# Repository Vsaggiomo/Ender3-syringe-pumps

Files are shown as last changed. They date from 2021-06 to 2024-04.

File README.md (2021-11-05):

# Ender 3 syringe pumps: 
open-source set of syringe pumps from an Ender 3 kit

**If you use the pump in your research, please cite:**

**Sander Baas, Vittorio Saggiomo,
Ender3 3D printer kit transformed into open, programmable syringe pump set,
HardwareX, Volume 10, 2021,
e00219, https://doi.org/10.1016/j.ohx.2021.e00219.**

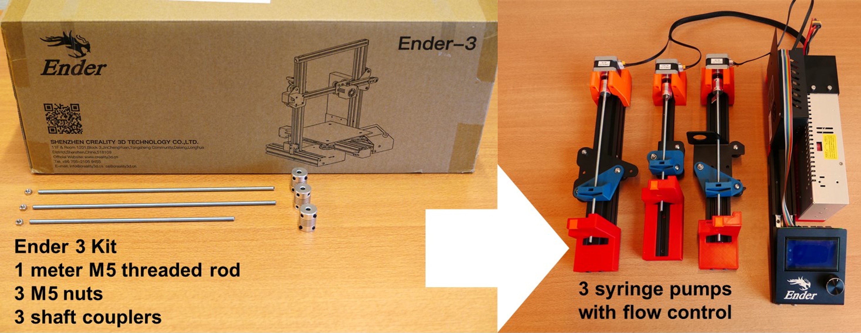
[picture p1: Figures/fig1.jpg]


Visit [**ChemRxiv**][2] for the preprint, and [**HardwareX**][3] for the published paper. 

A video of the project is here: https://www.youtube.com/watch?v=etUp4s1Bq-I

Ender 3 syringe pumps is an open source and open hardware device for converting an Ender 3 kit to a set of 3 syringe pumps. Almost everything needed for the build is the Ender 3 kit, even all the screws and the tools needed for the assembly. 
The only parts which needed to be bought are three 5x5 shaft couplers and M5 lead screw. 
All the 3D designs are in the /hardware folder. 

## Structure 
+ /hardware is a folder with the 3D printable files and a guide for the assembly 
+ /software is a folder with the instruction on how to use the pumps via gcode 
+ /videos are few video of the pumps in action

[1]: https://github.com/Vsaggiomo/Ender3-syringe-pumps/blob/main/Figures/fig1.jpg
[2]: https://chemrxiv.org/articles/preprint/Ender3_3D_Printer_Kit_Transformed_into_Open_Programmable_Syringe_Pump_Set/14718183 
[3]: https://doi.org/10.1016/j.ohx.2021.e00219

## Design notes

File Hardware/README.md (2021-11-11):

# Ender 3 syringe pumps: hardware

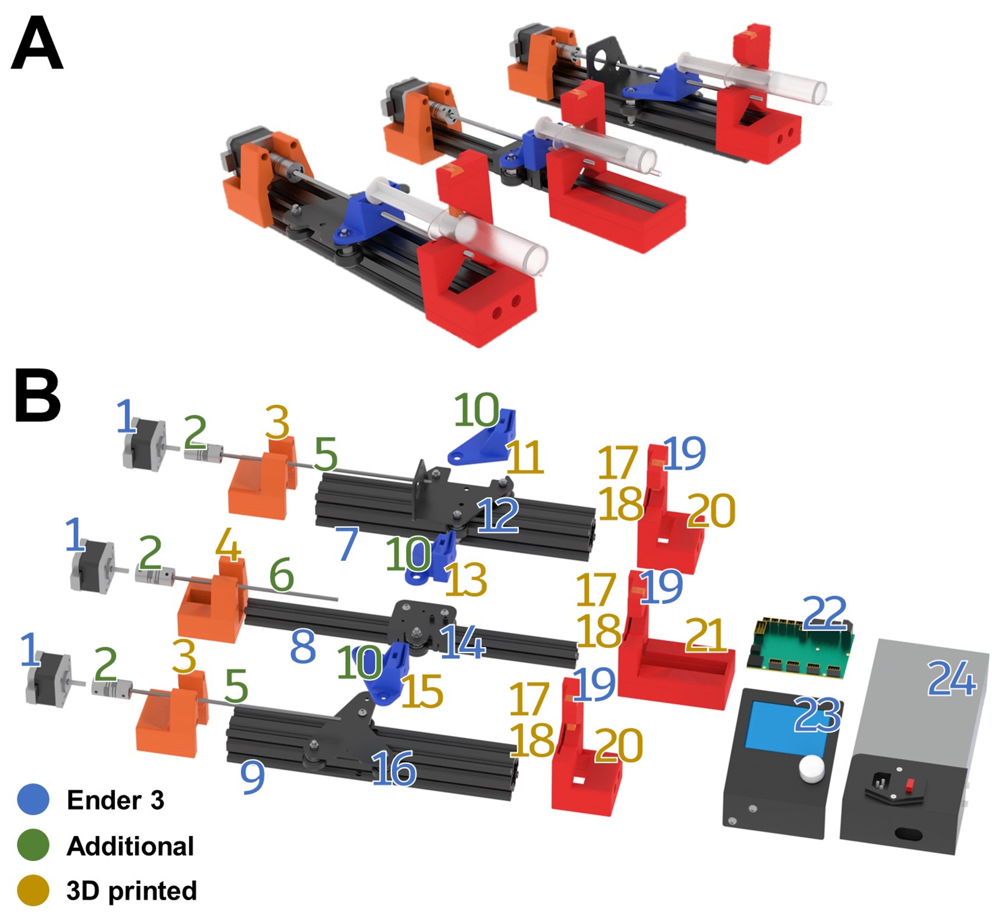
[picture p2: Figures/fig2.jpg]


+ STL and F3D contain the 3D printable files 
+ Ender 3 Syringe Pump Build Guide is the step by step guide to assemble the syringe pumps 

This design has been tested with Ender 3 and Ender 3 pro. It works also with the Ender 3 V2 with a small modification of the PSU mount, which can be found in the Ender3V2 directory. The Ender 3 V2 PSU mount was designed by Afonso Mendes (ammendes@igc.gulbenkian.pt) 

/STL/PressFitPulley.stl was designed by Jake_of_All_Trades https://www.thingiverse.com/thing:3593964/files 

UPDATE 05-11-2021: 50mL syringe adaptors are in /STL 

[1]: https://github.com/Vsaggiomo/Ender3-syringe-pumps/blob/main/Figures/fig2.jpg

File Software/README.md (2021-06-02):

# Ender 3 syringe pumps software 

+ Steps mL Calculation is an excel file for calculating the steps per mL of different syringes, using the diameter as input 
+ VideoS1 is a gcode example

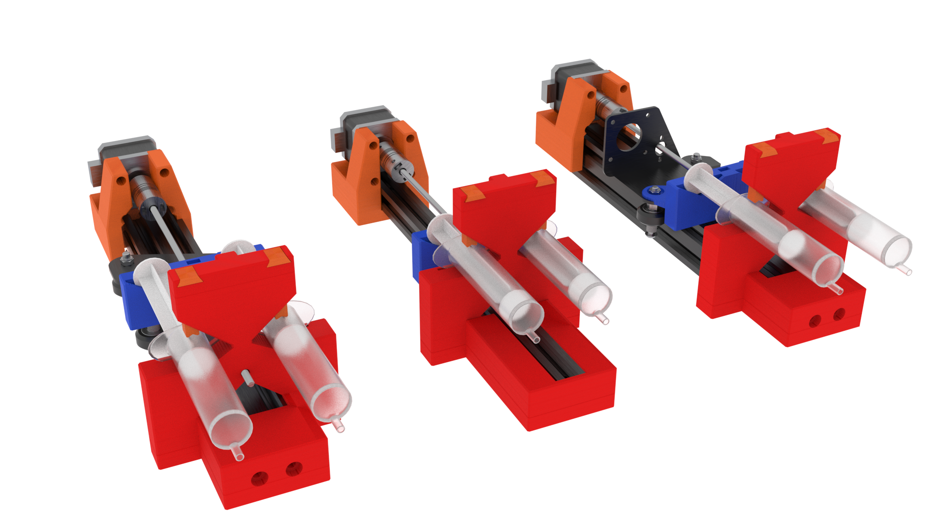
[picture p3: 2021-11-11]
Figures/double syringe.png

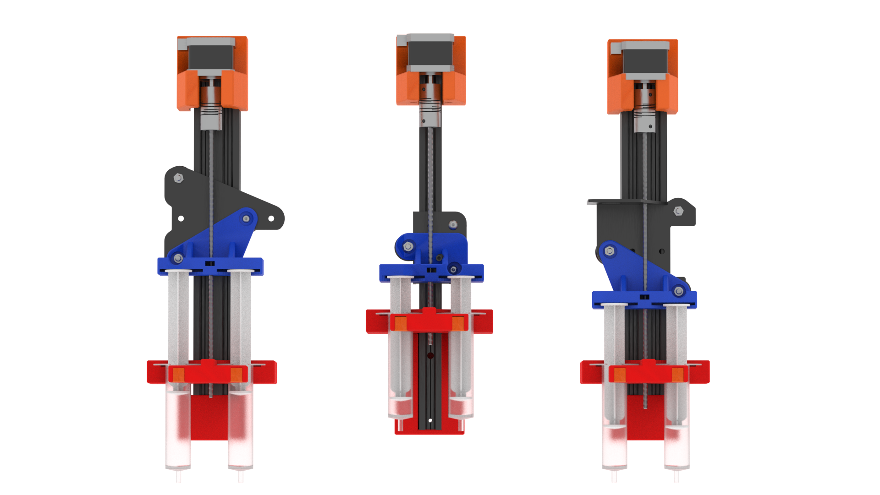
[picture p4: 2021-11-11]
Figures/double syinge2.png

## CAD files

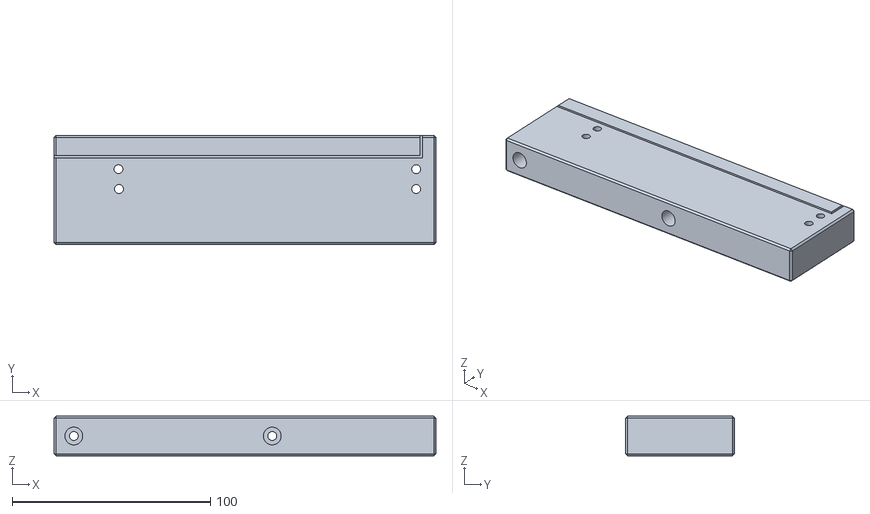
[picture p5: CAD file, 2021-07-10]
Hardware/Ender 3 V2/psu_mount_Ender3v2.stl
192.5 x 55.0 x 20.0

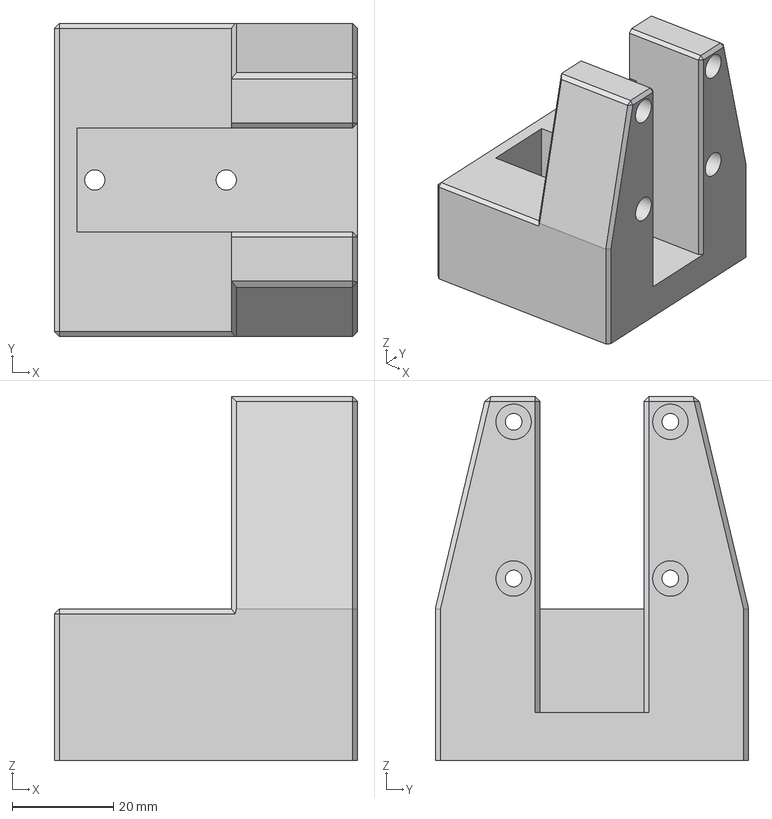
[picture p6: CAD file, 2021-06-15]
Hardware/STEP/E Stepper Mount v1.step
60.0 x 62.0 x 72.0 mm

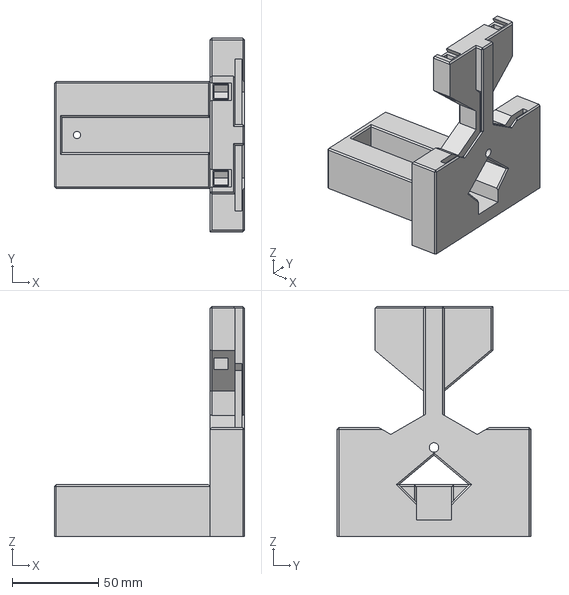
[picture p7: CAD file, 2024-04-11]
Hardware/STL/50 mL adaptors /E End Mount Dual 50 mL v1.step
110.0 x 112.0 x 133.0 mm

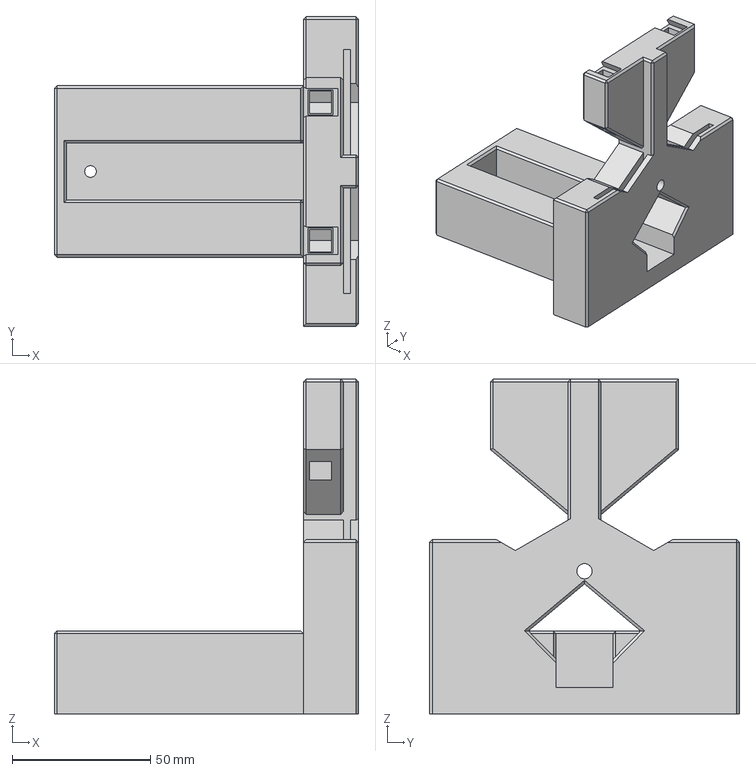
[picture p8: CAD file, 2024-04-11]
Hardware/STL/Double Syringe/E End Mount Dual v7.step
110.0 x 112.0 x 121.0 mm

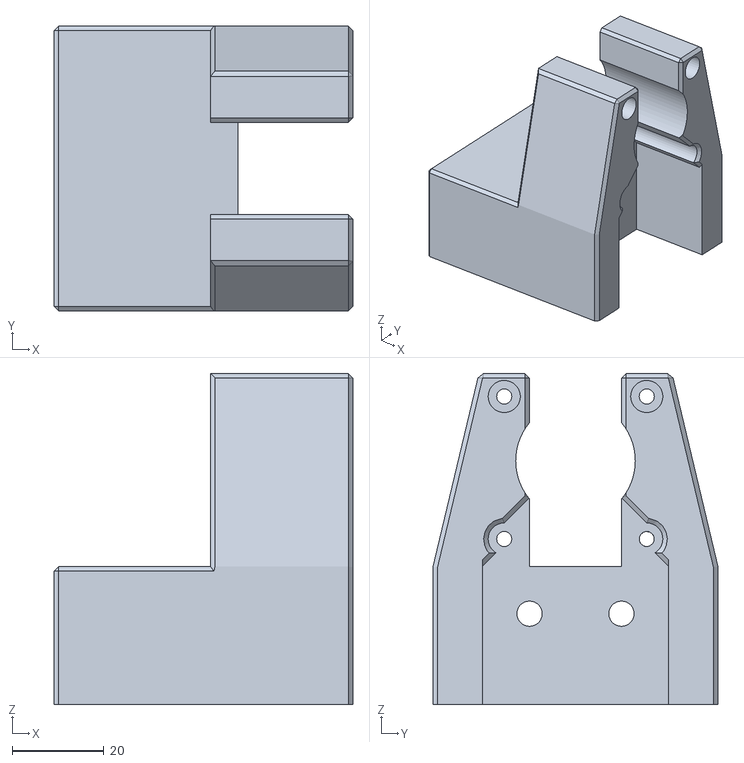
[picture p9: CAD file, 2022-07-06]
Hardware/STL/Large shaft coupler/X X Motor Stepper Mount Large Shaft Coupler v1.stl
65.0 x 62.0 x 72.0

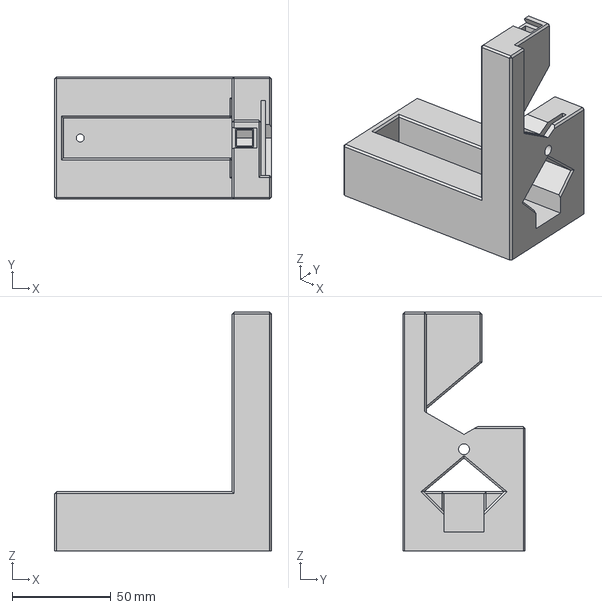
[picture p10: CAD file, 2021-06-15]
Hardware/STEP/E End Mount v1.step
110.0 x 62.0 x 121.0 mm

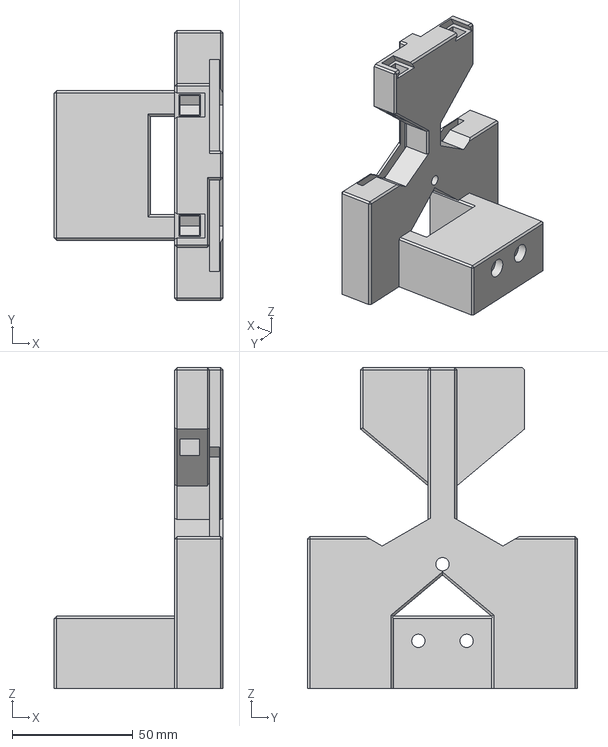
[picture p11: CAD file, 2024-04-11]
Hardware/STL/50 mL adaptors /X X Motor End Mount Dual 50 mL v4.step
70.0 x 112.0 x 133.0 mm

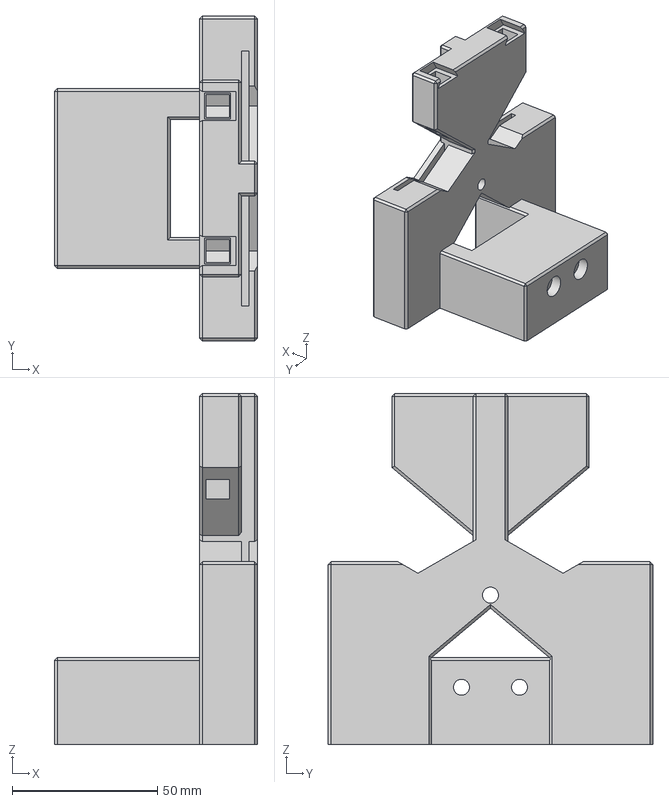
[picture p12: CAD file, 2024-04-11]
Hardware/STL/Double Syringe/X X Motor End Mount Dual v6.step
70.0 x 112.0 x 121.0 mm

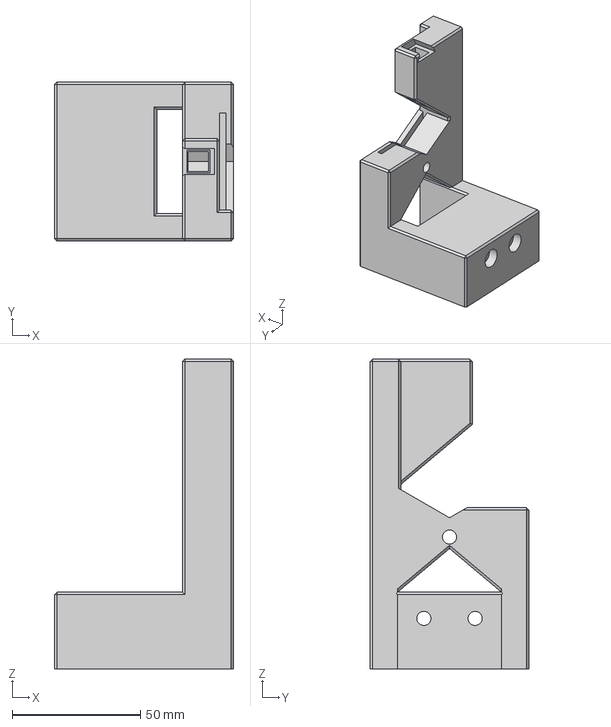
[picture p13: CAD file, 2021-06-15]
Hardware/STEP/X X Motor End Mount v1.step
70.0 x 62.0 x 121.0 mm

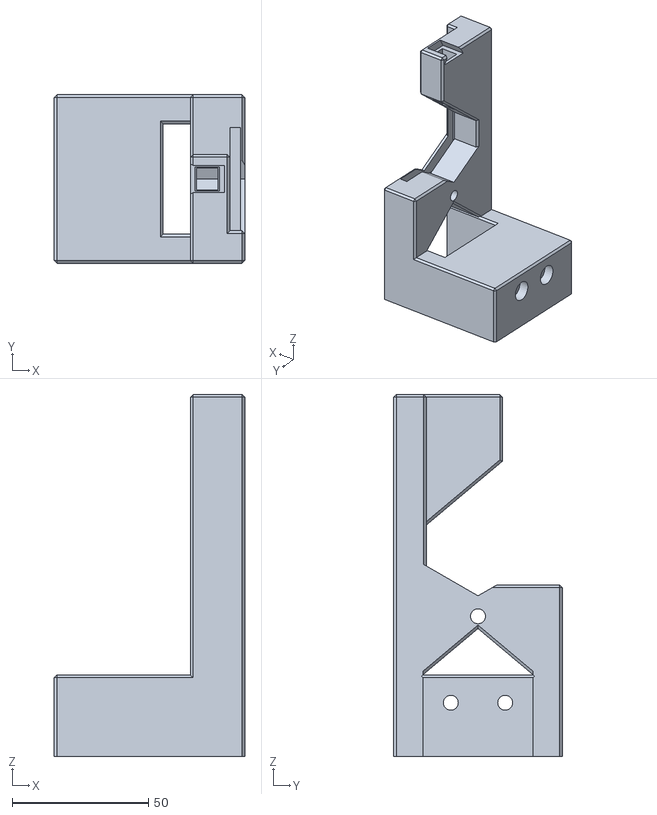
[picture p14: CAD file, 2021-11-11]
Hardware/STL/50 mL adaptors /X X Motor End Mount 50 mL.stl
70.0 x 62.0 x 133.0

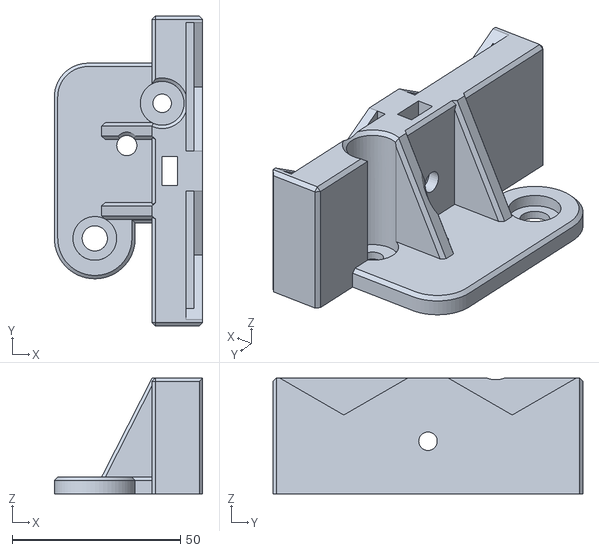
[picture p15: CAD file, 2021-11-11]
Hardware/STL/Double Syringe/E Slide Mount Dual.stl
44.0 x 92.0 x 34.4

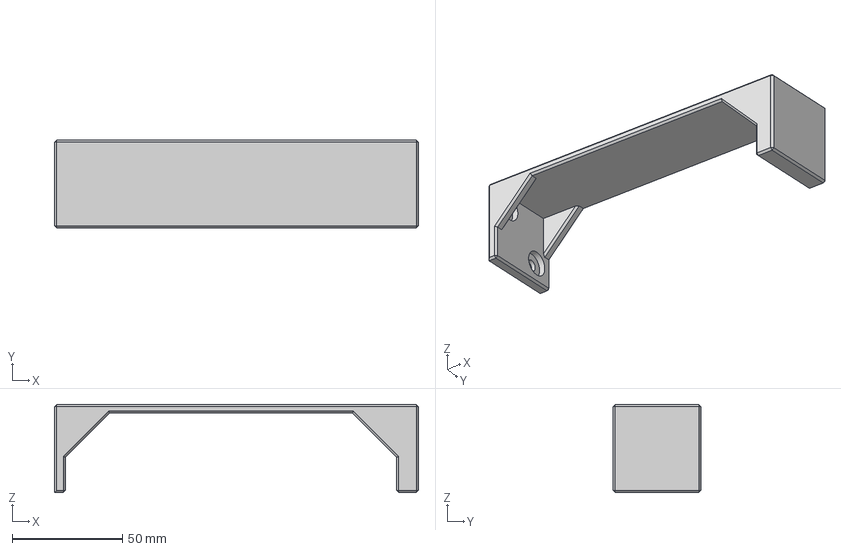
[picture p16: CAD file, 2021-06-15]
Hardware/STEP/Electronics Base v1.step
165.2 x 40.0 x 40.0 mm

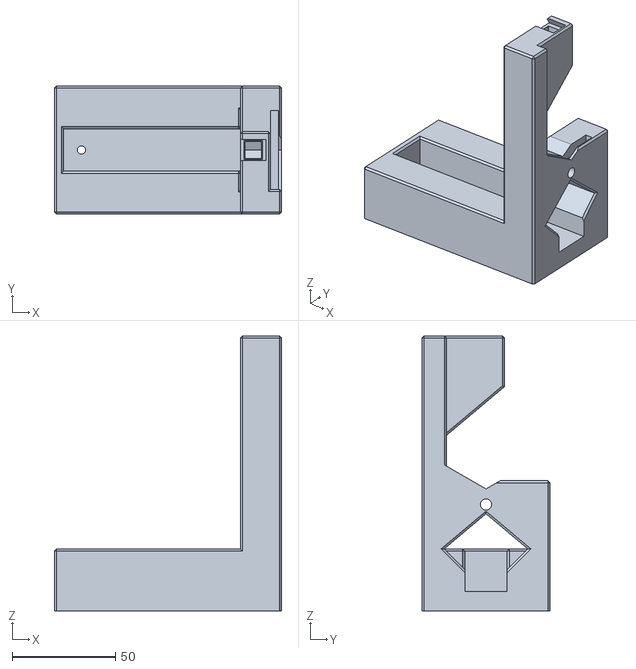
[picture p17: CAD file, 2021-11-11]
Hardware/STL/50 mL adaptors /E End Mount 50 mL.stl
110.0 x 62.0 x 133.0

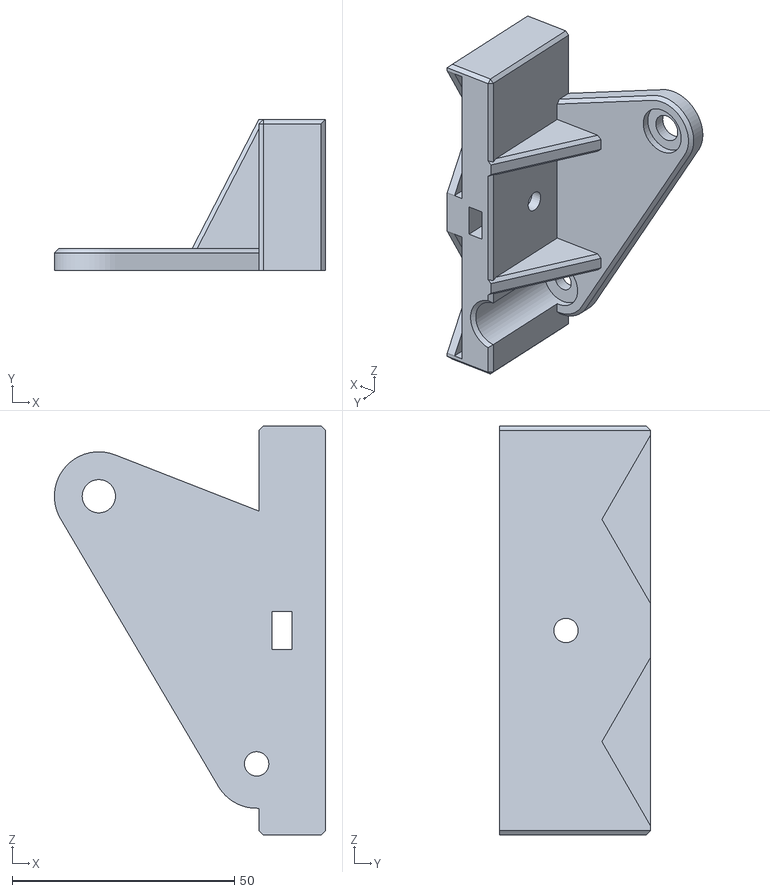
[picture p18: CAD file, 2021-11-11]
Hardware/STL/Double Syringe/X Motor Slide Mount Dual.stl
61.0 x 34.0 x 92.0

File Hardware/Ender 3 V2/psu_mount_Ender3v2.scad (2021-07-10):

$fa=5;
$fs=0.5;

difference(){
// Change this path to where you saved your original STL
import("/Users/ammendes/Documents/3D prints/Ender3_pumps/stl/PSU Mount v1.stl");

// Right screw hole
translate([182.5,28,0])
    cylinder(h=20, d=4.5);

// Left screw hole
translate([32.75,28,0])
    cylinder(h=20, d=4.5);

//Left screw head hole
translate([32.75,28,0])
    cylinder(h=7.5, d=9);

// Right screw head hole
translate([182.5,28,0])
    cylinder(h=7.5, d=9);

// Long horizontal gap
translate([0,43.5,15])  
    cube([184.5,1.3,5]);

// Short vertical gap
translate([184.5,43.5,15])
    cube([1.3,12,5]);
}

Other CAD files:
Hardware/STL/Large shaft coupler/E Stepper Mount Large Shaft Coupler v1.stl.stl
Hardware/STEP/X Motor Slide Mount v1.step
Hardware/STL/50 mL adaptors /X X Motor End Mount 50mL v2.stl
Hardware/F3D/50 mL adaptors/E End Mount 50 mL.f3d
Hardware/F3D/50 mL adaptors/E End Mount Dual 50 mL.f3d
Hardware/F3D/50 mL adaptors/X X Motor End Mount 50 mL.f3d
Hardware/F3D/50 mL adaptors/X X Motor End Mount Dual 50 mL.f3d
Hardware/F3D/Clamp Bar Long v1.f3d
Hardware/F3D/Clamp Bar Short v1.f3d
Hardware/F3D/Clamp Bar v1.f3d
Hardware/F3D/Double Syringe /E End Mount Dual.f3d
Hardware/F3D/Double Syringe /E Slide Mount Dual.f3d
Hardware/F3D/Double Syringe /X Motor Slide Mount Dual.f3d
Hardware/F3D/Double Syringe /X Slide Mount Dual.f3d
Hardware/F3D/Double Syringe /X X Motor End Mount Dual.f3d
Hardware/F3D/Dovetail Cap v1.f3d
Hardware/F3D/E End Mount v1.f3d
Hardware/F3D/E Slide Mount v1.f3d
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

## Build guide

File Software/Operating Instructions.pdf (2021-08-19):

Operating Instructions

The syringe pumps are controlled by the 3D printer motherboard, which is already flashed with Marlin software and therefore works with G-code. There are two ways of controlling the pumps: a) using a computer connected to the board via USB and using direct control software such as PronterFace or Octoprint, with the latter able to be used remotely via network. B) writing the G-code file, uploading it on a microSD card and using the printer interface for printing the file without the need of a computer attached to the pumps.
A G-code file is a set of instruction which Marlin interprets line by line and passes the operations to the motors. The file is a simple text file saved as .gcode. For controlling the pumps, a few G-code commands are needed:

M92 X<Steps per mm> Y<Steps per mm> Z<Steps per mm>

M92 should be at the start of the G-code, as this command will set the number of steps required for moving one axis one millimeter, which in the case of the Ender 3 motors/drivers and the M5x0.8 mm threaded rod is 4000 steps per mm. The Ender 3 uses stepper motors with a step angle of 1.8 °, or 200 steps per revolution. The TSMC2208 stepper drivers are set to 1/16 microsteps, which is the default setting for the Ender 3. The pitch of the leadscrew is 0.8 mm. This gives the value of 4000 steps per mm. However, as we are dealing with flows, we found that it is more user-friendly to change this command from steps per mm to steps per mL. This can be easily done by calculating the distance required to push a volume of 1 mL depending on the diameter of the syringe used. To do this, the inner diameter (I.D.) of the syringe needs to be determined. Next, the area of the plunger can be calculated. The linear syringe travel to deposit 1 mL can be calculated by dividing 1 cm³ by the plunger area (cm²
). Divide this number
by the steps per mm value (4000) to get the steps per mL. We have attached a simple calculator in the supplementary material to calculate the steps per mL using the diameter of a syringe as input. As an example, a 10 mL syringe has a diameter of 15.6 mm and the calculated steps required to move 1 mL are 20927, a 5 mL syringe has a diameter of 12.3 mm and the calculated
steps | are | 33663.
Another thing to take note of, is that in the normal configuration, the X and Y motors are inverted, so this should also be set in the M92 command by giving negative step/mm values. A M92 set up using two 5 mL syringes on the X and Z axes and a 10 mL syringe on the Y is therefore:

M92 X-33663 Y-20927 Z33663
This will set the number of steps per mL in such a way that the rest of the G-code will use this to calculate the pump movements.

M302 S0
This command will set the printer to move the motors without checking the temperature of the hot end. This is usually a 3D printer safety check for avoiding extruding material when there are some problems with the hot end. In this case the hot end is detached, so there is no risk of thermal runaway.

M211 S0
This command will disable the endstops which may cause problems as they are not connected.

G91
Use relative positioning. This is important when multiple movements are used, otherwise the motors will start from a 0.0.0 position and use that as reference point.

G4 S<time in seconds>
Pause the commands for a set amount of time.

G1 X<mL> Y<mL> Z<mL> F<mL/min>
This is the command to move the syringe pumps at certain flowrates. As we set up the steps/mL in the M92 command, now all the G1 codes are in mL/min. This can be a positive number or a negative number, positive for pushing and negative for retracting.

For example:
G1 X0.5 F1
Will use syringe pump X and will deliver 0.5 mL of liquid at a speed of 1 mL per minute. Multiple syringes can be used at the same time:
G1 X0.5 Y0.5 Z0.5 F1
Will deliver, at the same time, 0.5 mL of liquid from the pumps on X, Y, and Z at a speed of 1 mL/min
For using different flow speed for different pumps, the total amount of liquid should be calculated taking in account that all the pumps will reach the end at the same time. For example: G1 X2 Y1 Z2 F1
Will deliver the set amount of liquid at different flow speed, using 1ml/min on Y, and 2mL/min on X and Z.
For commenting on G-code files the “;” character should be used. This can be useful in commenting the G-code with metadata.

An example of full G-code (VideoS1):
; Experiment 01 20/05/2021
; 10 mL syringes on the three pumps
M92 X-20927 Y-20927 Z20927 ; set the proper steps/mL for the 10mL syringe M302 S0 ; print without checking temperature
G91 ; relative positioning
; deliver 1mL at 2mL/min sequentially
G1 X1 F2
G1 Y1 F2
G1 Z1 F2
; wait for 10 seconds
G4 S10
; deliver 1mL on X and Z at 1mL/min, 2mL on Y at 2mL/min G1 X1 Y2 Z1 F1
; wait 10 seconds
G4 S10
; deliver 1mL at 2mL/min sequentially G1 Z1 F2
G1 Y1 F2
G1 X1 F2

Without previous knowledge in programming and in a few lines of G-code it is possible to program the syringe pumps to do multiple operations. This file can now be saved as .gcode, uploaded on a microSD card, and run on the Ender 3 syringe pumps. Or it can be sent using a computer connected to the USB.
G-code files can be easily shared between labs for improving reproducibility of experiments.

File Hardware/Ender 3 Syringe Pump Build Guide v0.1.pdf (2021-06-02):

## Ender 3 Syringe Pump Build Guide

In this build guide, the build process of the Ender 3 based pump system will be explained. Assembly instructions, as well as indications of how to disassemble and reuse existing parts will be given. The guide consists of 37 steps and will result in three pump channels, as well as a Control Unit.

### Step 1: Layout

Start with laying out all the parts and part bags included in the kit (figure 1).

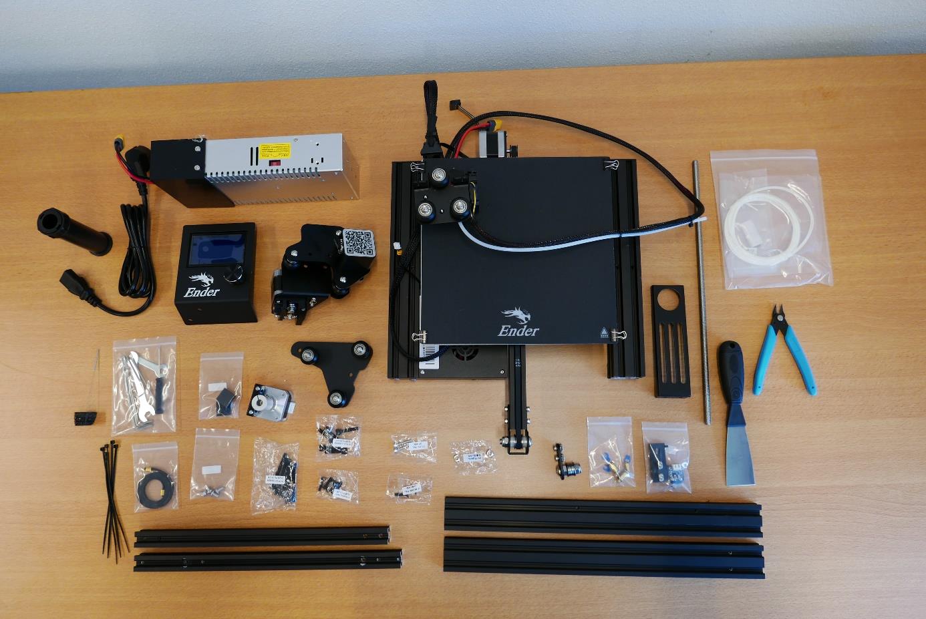
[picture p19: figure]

Figure 1 All parts included in the Ender 3 kit.

### Step 2: Collect the necessary parts for the E Plate Pump frame

To build the Extruder Plate Pump frame, take the extruder head, the long 20x20 mm rail, the bag of M4x16 machine screws and the 3D printed parts for this pump channel.

Figure 2 Necessary parts to build the Extruder Plate Pump Channel frame: Extruder head, M4x16 screws, 20x20 rail, E End Mount, E Slide Mount, E Stepper Mount, Clamp Bar and Dovetail Cap.

### Step 3: Remove unused parts from the E Plate and mount

To prepare the E Plate, remove all the unnecessary parts. Start by removing the two M3 screws (save these screws for later use) (fig 3B). Now remove the hotend shroud/fan mount. Next, remove the hotend (fig 3C). Finally, remove the two screw indicated in red circles (fig. 3D). The E Plate is now ready to be used in the pump channel.

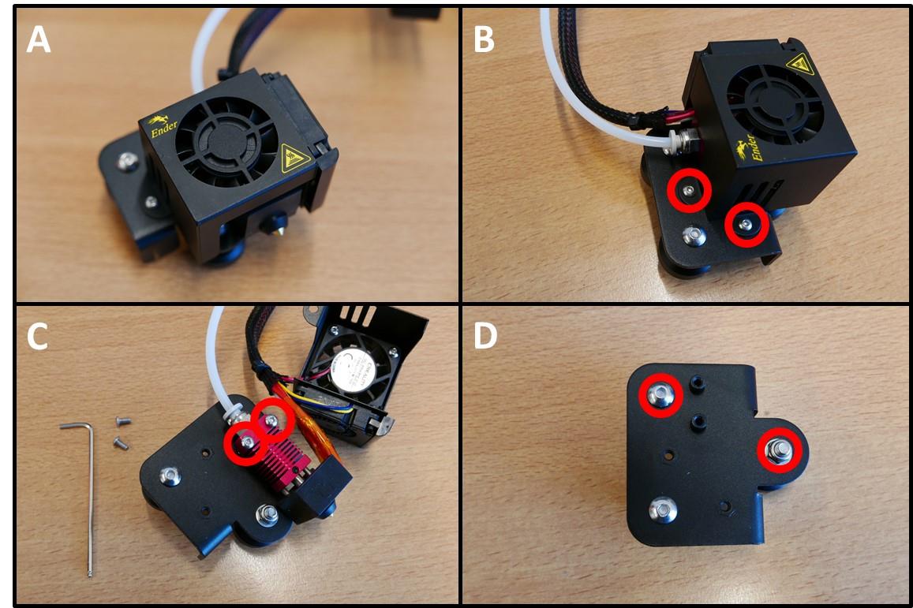
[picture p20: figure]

Figure 3 Preparing the E Plate for use in the pump. A) Extruder head overview. B) Removal of hotend shroud screws. These screws need to be saved for later use. C) Removal of the hotend. D) Loosening two screws in preparation for the Slider Mount.

### Step 4: Install the E Slide Mount on the E Plate

Take the E Slide Mount and fit it on the Extruder Plate (fig. 4A), by replacing the two removed screws from figure 3D. Note the eccentric hexagonal adjuster that will be used later to remove slop in rail guidance mechanism.

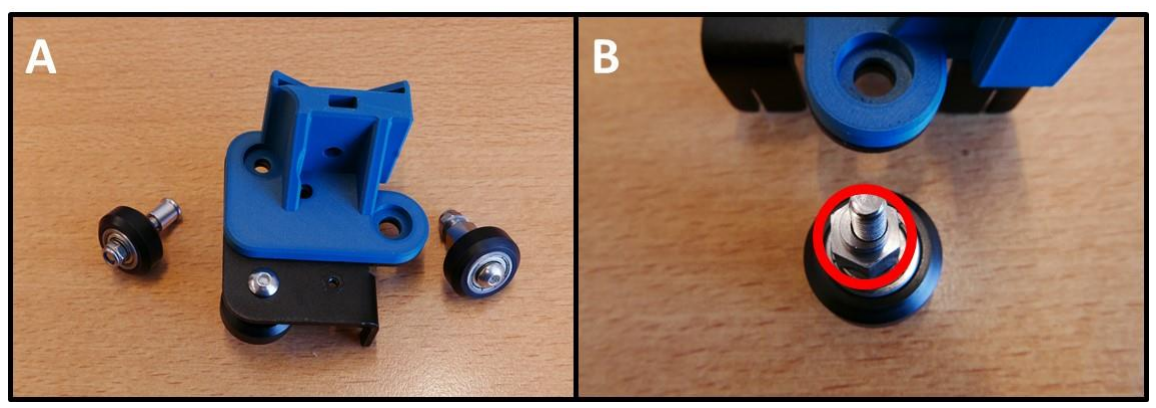
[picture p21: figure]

Figure 4 Mounting the E Slide Mount. A) E Slide mount fitted to the E Plate. B) Eccentric adjuster for the guidance mechanism.

### Step 5: Install the E Stepper Mount

Install the E Stepper Mount using the M4x16 screws (fig. 2). Slide the mount onto the rail and tighten the screws on the bottom (fig. 5C).

Figure 5 E Stepper Mount installation procedure. A) E Stepper Mount and 20x20 rail. B) Rail slides into E Stepper Mount. C) E Stepper Mount secured with M4x16 screws.

### Step 6: Install E Slide Mount on rail

Install the E Slide Mount assembly onto the rail, with the 3D printed mount facing away from the E Stepper Mount. Adjust the tension on the rollers by turning the eccentric hexagonal nut (fig. 6).

Figure 6 Tension adjustment of the E Slide Mount rollers.

### Step 7: Install the E End Mount

Finish the frame of the E Plate Pump by installing the E End Mount. Slide the mount on the rail (fig. 7A) and use the remaining M4x16 screws to attach the mount (fig. 7B).

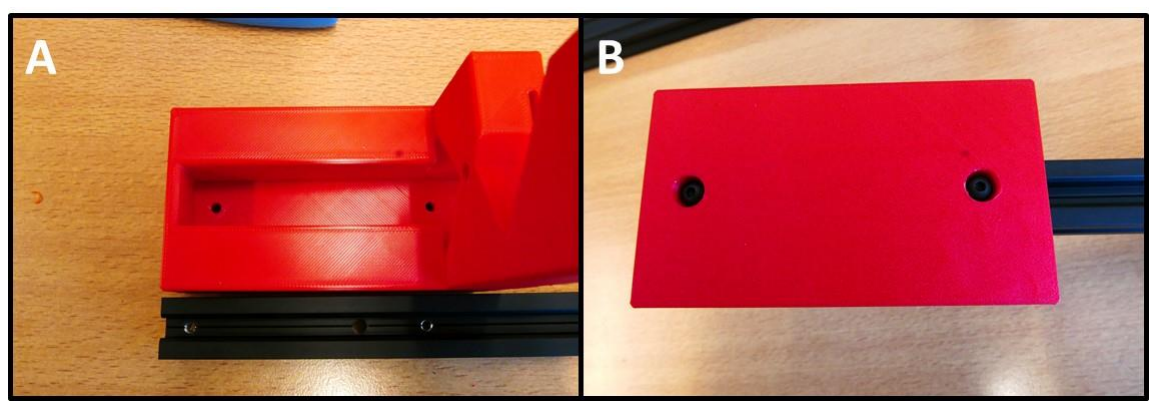
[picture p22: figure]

Figure 7 A) E End Mount next to 20x20 rail. B) E End Mount fastened using 2 M4x16 screws.

### Step 8: Remove unnecessary parts from stepper motor

Take the stepper motor shown in figure 8A. Remove the screws circled in red (fig. 8B). Then, loosen the grub screws in red (fig. 8C) and remove the coupler. The stepper motor is now ready (fig. 8D).

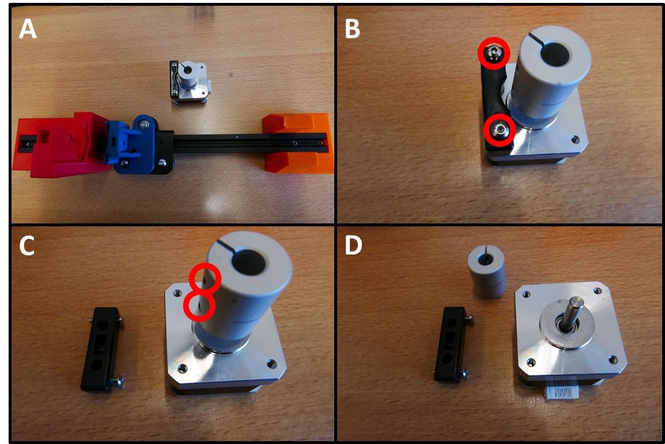
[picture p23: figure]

Figure 8 Preparing the stepper motor for installation. A) Overview of the E Plate pump and stepper. B) Removal of bracket.
C) Removal of shaft coupler. D) Stepper ready for use in pump.

### Step 9: Install stepper motor on the E Stepper Mount

The stepper motor is now to be installed on the E Stepper Mount. For the installation, 4 M3x6 screws are required. These can be taken from the Y stepper motor, shown in figure 9A. Save the Y stepper for later use. Figure 9B shows the E Stepper Mount, the stepper motor to be installed and the M3x6 screws. These screws can be inserted in the counterbored holes of the E Stepper Mount and tightened, to affix the stepper motor.

Figure 9 Stepper motor mounting. A) Gathering M3x6 screws from the Y stepper. B) All parts to be combined. C) Stepper motor mounted on the E Stepper Mount.

### Step 10: Cut the M5 threaded rod to size

For the drive rod, an M5 threaded rod needs to be cut to size. This can be done using a hacksaw or a power tool such as a cutoff wheel. Before starting the cut, thread on an M5 nut onto the rod. Cut the rod and clean off the sharp end with a file or sandpaper. After cutting and filing, the nut can be threaded over the cut end. This will straighten out the threads. 2 rods of 27 cm and 1 rod of 22 cm are needed to complete all three pumps (fig. 10).

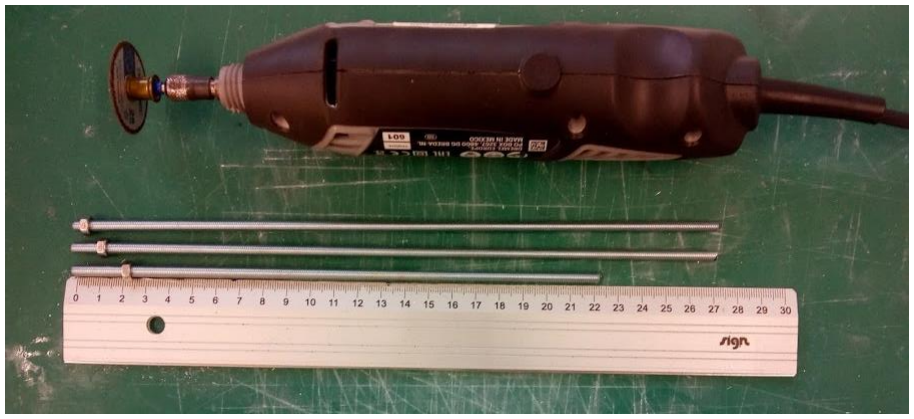
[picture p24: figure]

Figure 10 M5 Threaded rods cut to length. Two 27 cm rods for the X Plate and X Motor Plate pumps, 22 cm rod for the E Plate pump.

### Step 11: Install the threaded rod

To install the threaded rod, take the 22 cm threaded rod, 1 M5 nut and a shaft coupler (fig. 11A). Install the shaft coupler onto the stepper motor by tightening the two grub screws (fig. 11B). Slide the threaded rod through the E End Mount, up to the E Slide Mount. Lay the assembly on it’s side and push in the nut, centering it with the through-hole for the rod (fig. 11C). Thread the rod through the nut, all the way up to the shaft coupler. Tighten the grub screws to install the threaded rod (fig. 11D).

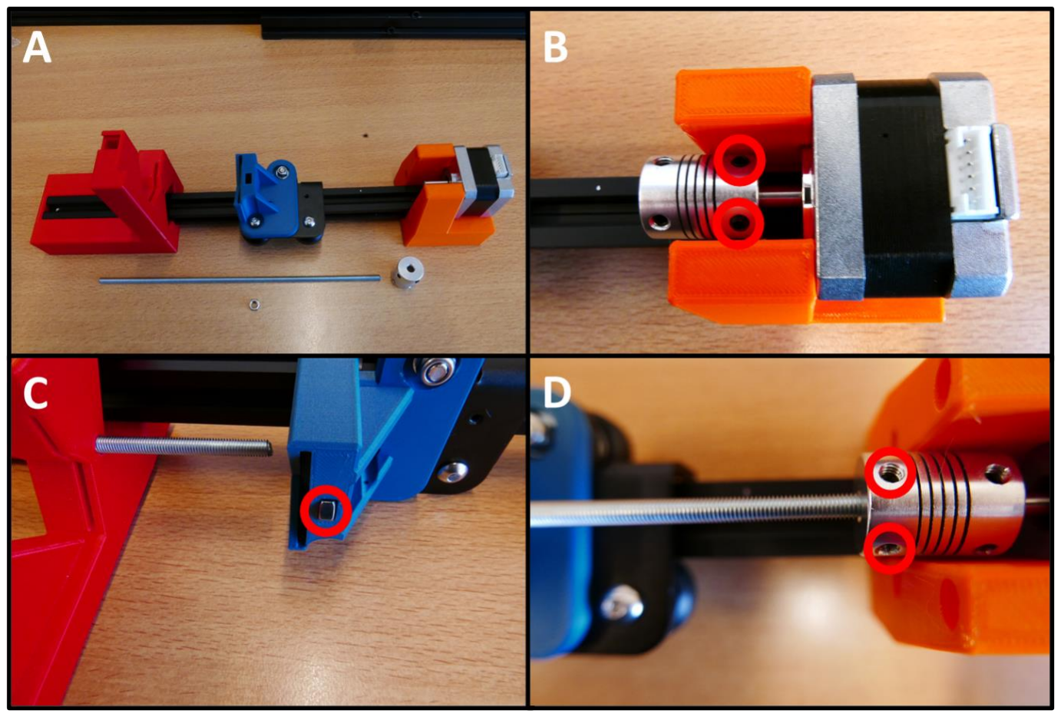
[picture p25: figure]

Figure 11 Installation of the threaded rod and shaft coupler. A) All components laid out. B) Shaft coupler installation. C) Fixing the threaded rod to the E Slide Mount using an M5 nut. D) Threaded rod clamped in the shaft coupler.

### Step 12: Collect the springs for the syringe clamp

To clamp the syringes in place, the springs from the bed levelling mechanism will be used. Start by removing the clips and printbed cover (fig. 12A). Unscrew the large plastic wheel (fig. 12B). Next, remove the machine screw to free up the spring (fig. 12C). The spring can now be removed (fig. 12D). Repeat this process to collect 3 springs in total.

Figure 12 Obtaining the springs for the syringe clamp mechanism. A) Remove the spring clips holding the printbed cover. B) Remove the plastic handwheel. C) Remove the machine screw. D) The spring can now be removed and used in the pump.

### Step 13: Install the syring clamp mechanism

The syringe clamping mechanism can now be installed. This mechanism consists of a Clamp Bar, Dovetail Cap and one of the springs (fig. 13A). Slide the clamp bar into the slot on top of the E End Mount (fig. 13B). Next, place the spring on top, in the square hole (fig. 13C). Finally, close the top with a Dovetail Cap. The pump channel is now ready to be used. Different length Clamp Bars can easily be exchanged to accommodate different syringe diameters.

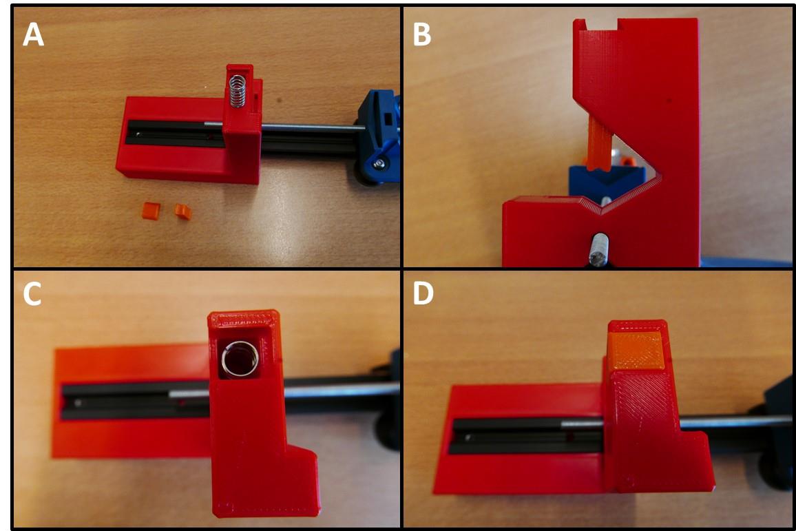
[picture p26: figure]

Figure 13 Fitting the syringe clamping mechanism. A) The necessary parts: Spring, Clamp Bar and Dovetail Cap. B) Clamp Bar installed in the slot. C) Spring placed on top of the Clamp Bar. D) The slot closed off with a Dovetail Cap, securing the mechanism in place.

### Step 14: Collecting the 40x40 rails

To build the X Motor Plate pump, a 40x40 rail is needed from the Ender 3 frame (fig. 14A). Loosen the two M5x45 screws that are holding this piece and save the screws (fig. 14B). Use one of the hex wrenches to push out the end cap (fig. 14C).

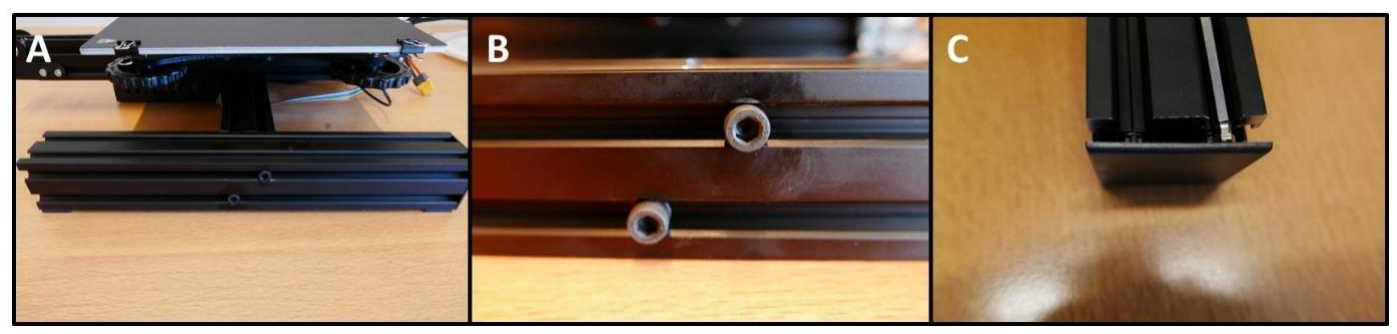
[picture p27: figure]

Figure 14 Gathering the 40x40 rail. A) The rail still mounted to the Ender 3 base. B) Loosen the M5x45 screws to remove the rail. C) Using a hex wrench, the end cap can be pushed out.

For the X Plate pump another 40x40 rail is need, from the other side of the base. Loosen the M5x45 screws (fig. 15A) and save them. Then, also remove the electronics case by removing the two screws (fig. 15B). Save these screws as well. Remove the end cap on the rail like in figure 14C.

Figure 15 Gathering the second 40x40 rail. A) Removing the M5x45 screws. B) Removing the electronics case.

### Step 15: Collect the parts for the X Motor Plate Pump

To build the X Motor Plate Pump, take the X Motor Assembly, 40x40 rail, X X Motor End Mount, X Motor Plate Slide Mount, X X Motor Stepper Mount, Clamp Bar, Dovetail cap and four M5x45 screws (fig. 16).

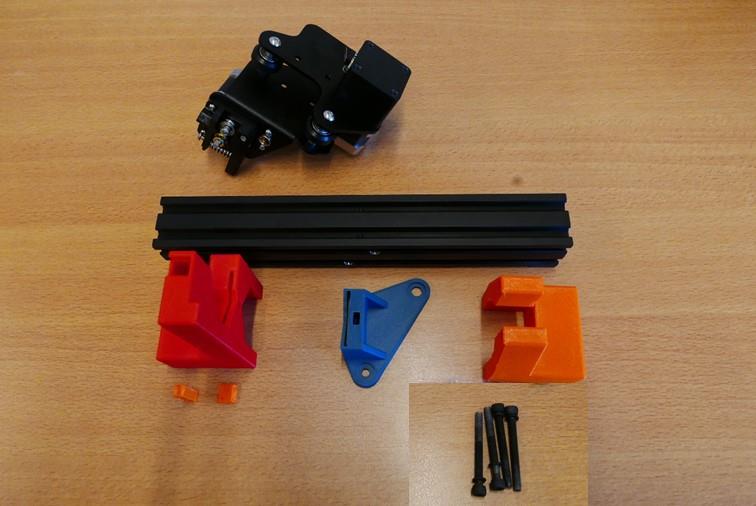
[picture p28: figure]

Figure 16 The parts needed to build the X Motor Plate pump.

### Step 16: Remove unnecessary parts from X Motor Assembly

The X Motor assembly consists of many parts, that need to be removed in order to use the X Motor Plate in the pump. Start by removing the sticker covering the screws (fig. 17A). Next, remove the roller screws holding the two plates together (fig. 17B). Remove the screws from the pulley cover (fig. 17C). Save the stepper motor for later use (fig. 17D). Next, remove all the screws indicated in red in figure 17E, remove the spring as well. Finally, remove the last two screws holding the filament clamping mechanism in place (fig. 17F). Save four M3x10 screws for later use (fig. 18).

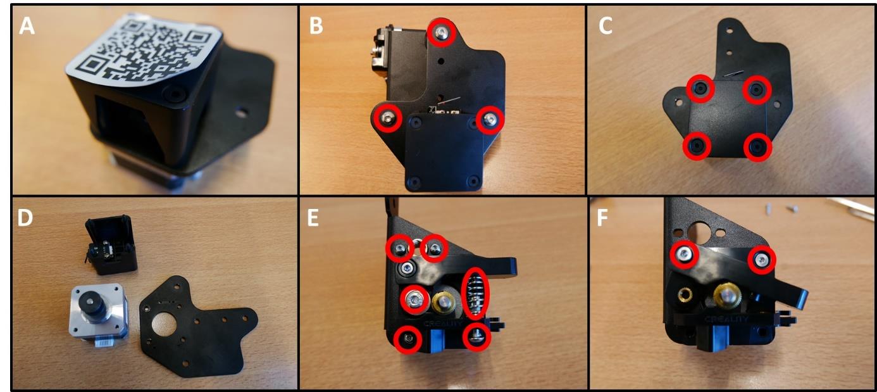
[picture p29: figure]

Figure 17 Procedure for disassembling the X Motor Assembly. A) Peel away the sticker. B) Remove the three roller screws. C) Remove the pulley cover. D) The freed up parts. Save the stepper motor. E) Remove all screws and the spring indicated in red. F) Remove the screws holding the filament clamp in place.

Figure 18 M3x10 screws to be used for later steps in the build guide.

### Step 17: Install the X Motor Slide Mount on the X Motor Plate

Take the angle bracket X Motor Plate and mount the X Motor Slide Mount, similar to step 4 (fig. 19A). Slide the mount onto the 40x40 rail and adjust the tension. Make sure the countersunk holes on the rail are on the side of the single guide wheel (fig. 19B).

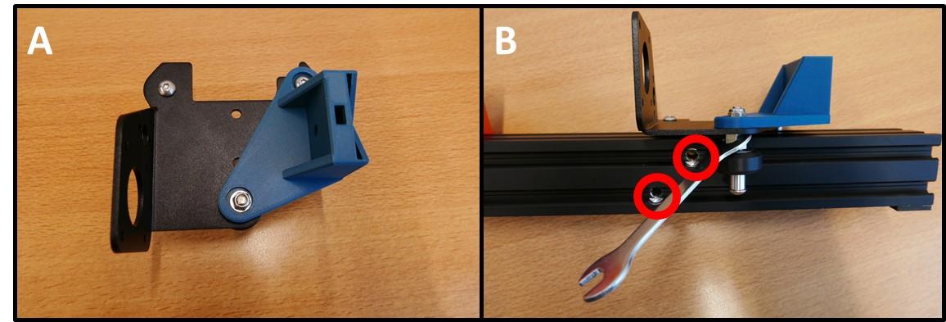
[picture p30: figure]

Figure 19 Installing the X Motor Slide Mount. A) 3D printed part mounted on the X Motor Plate. B) Fitting the assembly on the rail.

### Step 18: Removing the press-fit pulleys from the X and Y Motor

Take the X Stepper from step 16 and Y Stepper from step 9. They have press-fit pulleys that need to be removed. This can be accomplished by using a pulley removal tool. A 3D printed version is available from https://www.thingiverse.com/thing:3593964. Print this tool at 100% infill (fully solid). To use the tool, an M5 nut and M5x45 screw can be used (fig. 20A). Press the M5 nut into the hexagonal slot (fig. 20B) and thread in the screw. Slide the tool around the pulley and align the screw with the stepper shaft. Turn the screw to apply pressure on the shaft (fig. 20C). With the pulley removed, the stepper is ready to be used in the pump (fig. 20D). Repeat this process for the second stepper.

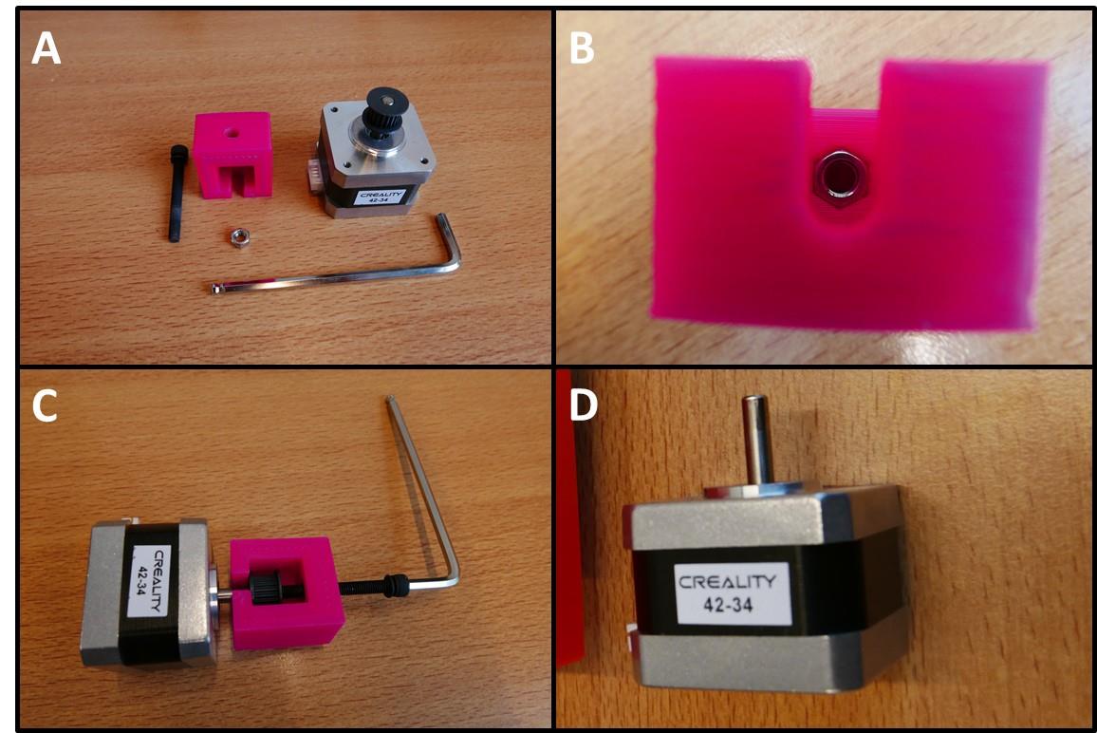
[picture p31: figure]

Figure 20 Stepper pulley removal process. A) Overview of the tool, parts and stepper. B) Fitting the M5 nut in the tool. C) Removing the pulley with the tool. D) Stepper motor ready for use in the pump.

### Step 19: Install the X X Motor Stepper Mount

Slide the X X Motor Stepper Mount on the 40x40 rail and insert the M5x45 screws (fig. 21A). Fasten the screw, the X X Motor Stepper Mount is now attached (fig. 21B).

Figure 21 Installing the X X Motor End Mount. A) Fitting the mount on the rail. B) Fully installed.

### Step 20: Install the X X Motor End Mount

Place the X X Motor End Mount on the opposite end of the 40x40 rail. Fasten the part with two M5x45 screws (fig. 22).

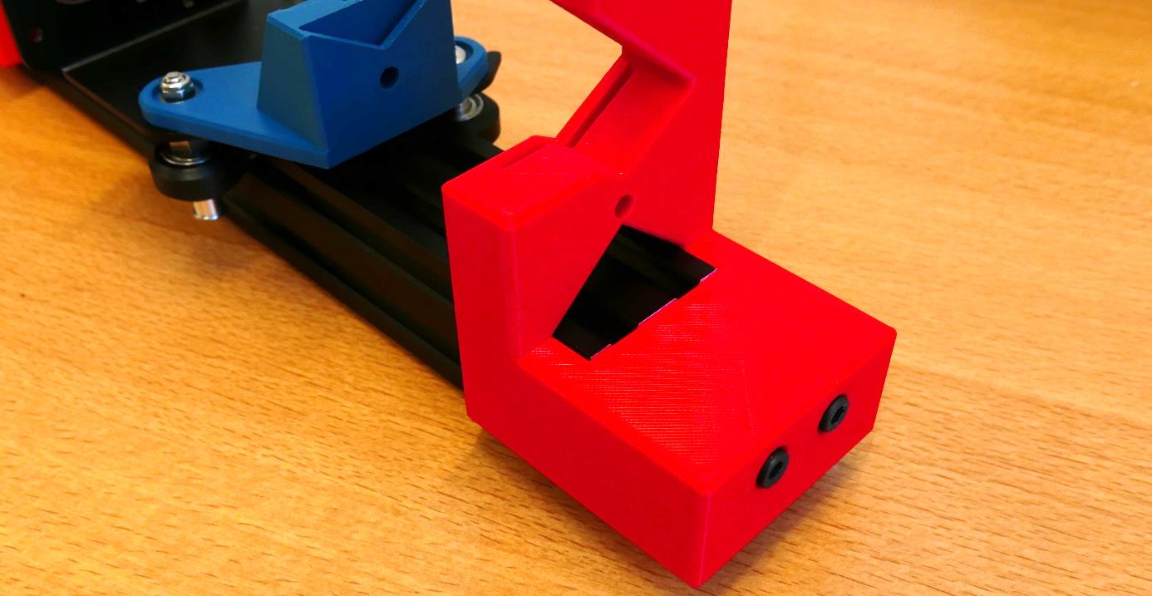
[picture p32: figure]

Figure 22 The installed X X Motor End Mount.

### Step 21: Install the stepper motor

Install the stepper motor on the X X Motor Stepper Mount. Take 4 M3x1- screws by dismounting the Extruder Fan from the shroud (fig. 23A). Use these screws to install the stepper motor (fig. 23B).

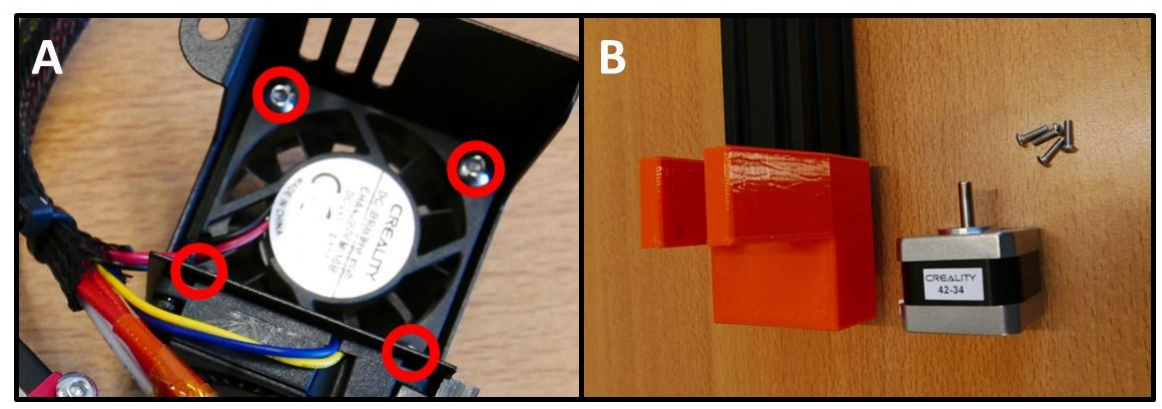
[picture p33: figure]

Figure 23 The stepper motor will be mounted with M3x10 screws. A) Take the M3x10 screws from the fan mounted on the extruder head. B) Ready to install the stepper motor.

### Step 22: Install the threaded rod

Take one of the 27 cm threaded rods from step 10 and install it in the X Motor Plate pump, follow the procedure from step 11. The end result looks like figure 24.

Figure 24 Installed threaded rod in the X Motor Plate pump.

### Step 23: Install the syringe clamp mechanism

Follow step 13 and install the syringe clamp mechanism. The X Motor Plate pump channel is now finished (fig. 25).

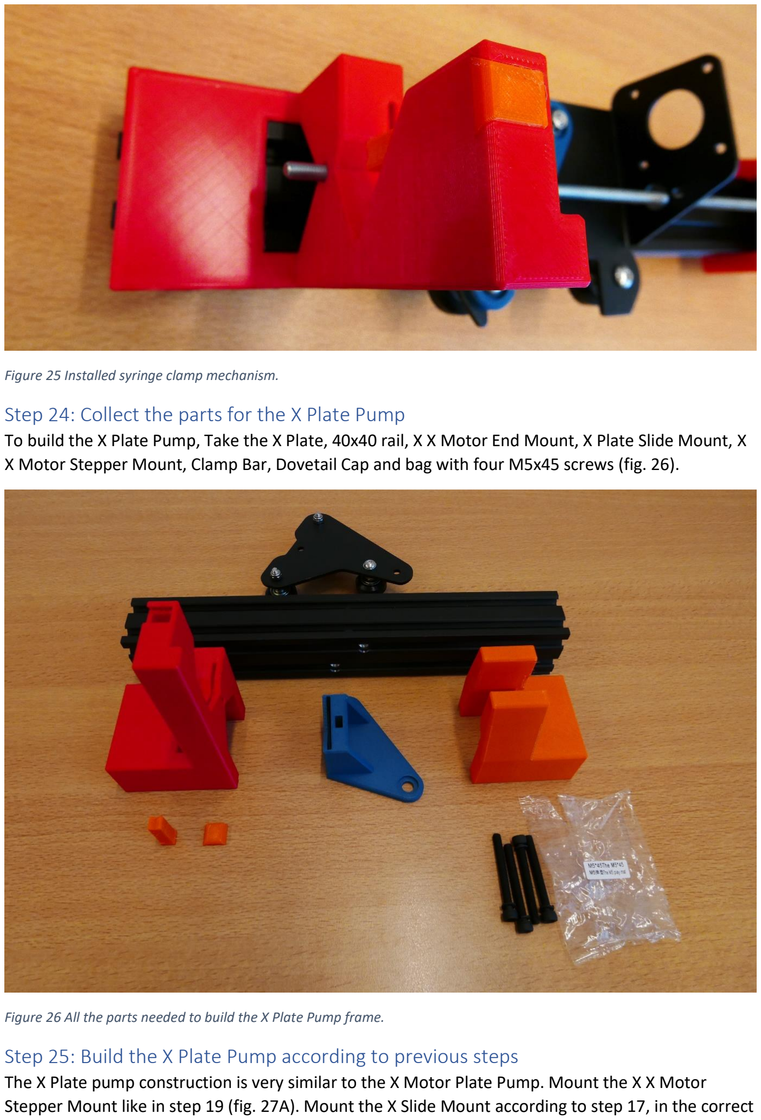
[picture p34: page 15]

Figure 25 Installed syringe clamp mechanism.

### Step 24: Collect the parts for the X Plate Pump

To build the X Plate Pump, Take the X Plate, 40x40 rail, X X Motor End Mount, X Plate Slide Mount, X X Motor Stepper Mount, Clamp Bar, Dovetail Cap and bag with four M5x45 screws (fig. 26).

Figure 26 All the parts needed to build the X Plate Pump frame.

### Step 25: Build the X Plate Pump according to previous steps

The X Plate pump construction is very similar to the X Motor Plate Pump. Mount the X X Motor Stepper Mount like in step 19 (fig. 27A). Mount the X Slide Mount according to step 17, in the correct orientation (fig. 27B) and slide onto rail (fig. 27C). Install the X X Motor End Mount following step 20 (fig. 27D). The X Plate Pump frame is now finished (fig. 27E).

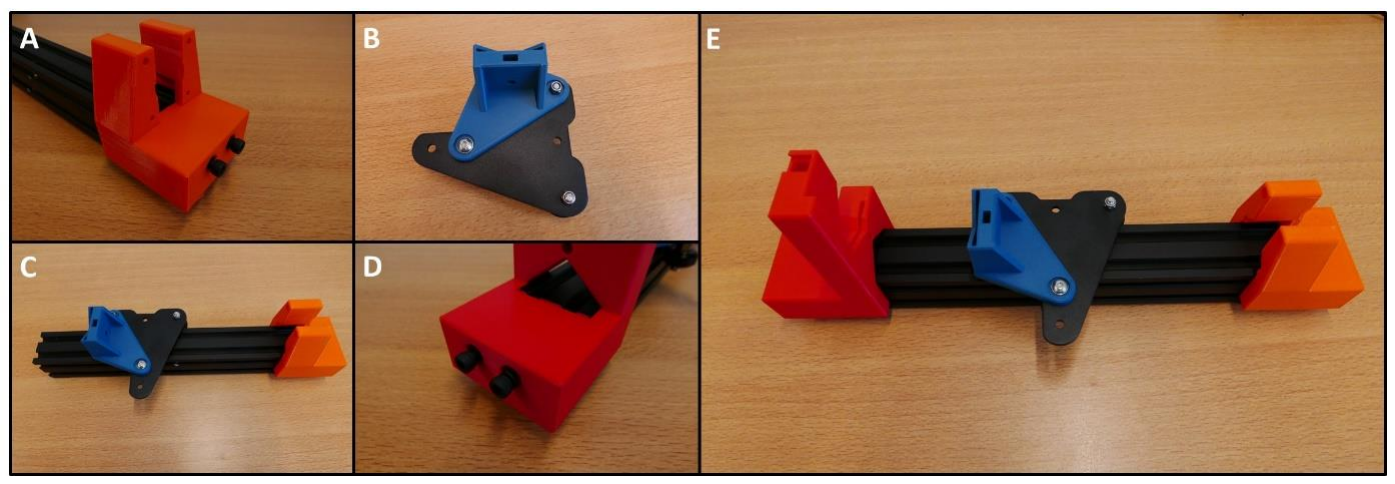
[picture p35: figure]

Figure 27 Building the X Plate Pump frame. A) X X Motor Stepper Mount installation. B) X Slide Mount orientation. C) Rail assembly D) Fastening the M5x45 screws on the X X Motor End Mount. E) Completed X Plate Pump frame.

### Step 26: Install the stepper motor

Install the stepper motor using the four M3x10 screws that were saved in step 16, according to the procedure of step 21 (fig. 28).

Figure 28 Stepper motor installed in the X Plate Pump frame.

### Step 27: Install the threaded rod

Take one of the 27 cm threaded rods from step 10 and install it in the X Plate pump, follow the procedure from step 11. The end result looks like figure 29.

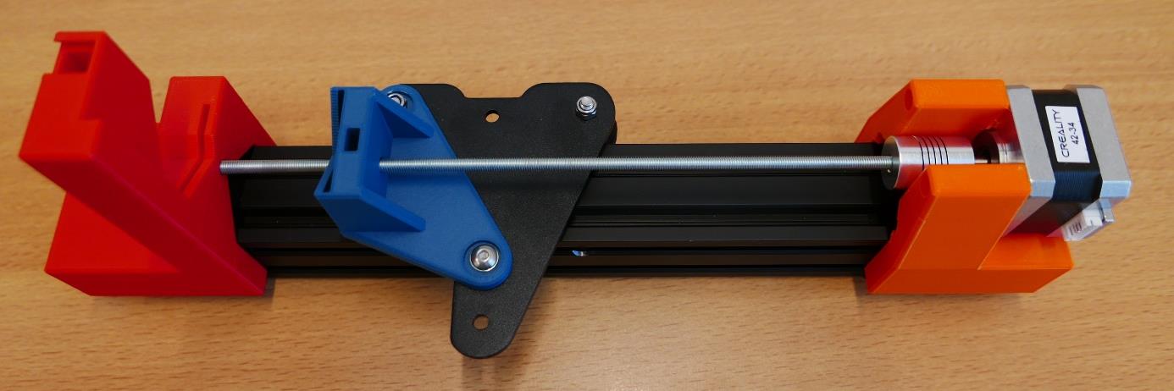
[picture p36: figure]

Figure 29 Threaded rod installed in the X Plate Pump.

### Step 28: Install the syringe clamp mechanism

Follow step 13 and install the syringe clamp mechanism. The X Plate pump channel is now finished (fig. 30).

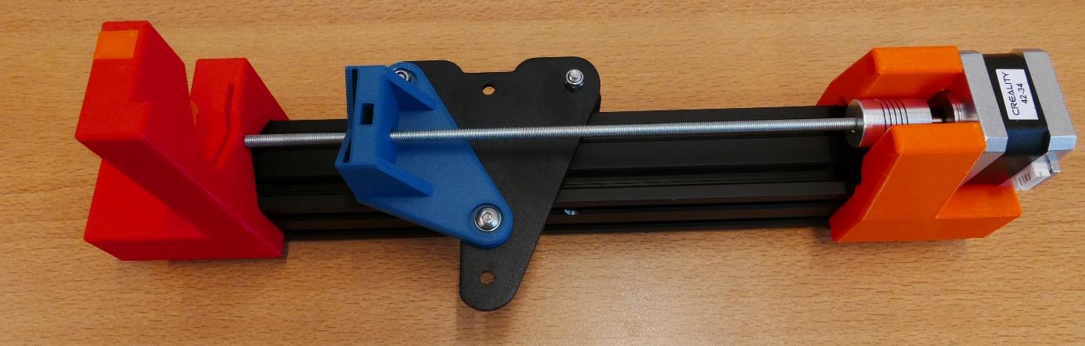
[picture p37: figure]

Figure 30 The completed X Plate Pump.

### Step 29: Detaching the Electronics Box

Take the remainder of the Ender 3 base and flip it over (fig. 31A). Detach the cable from the Y limit switch (fig. 31B). Remove the M5x45 screws to free up the 40x40 rail (fig. 31C). Keep the rail for later use. Remove the screw on the fan-side of the Electronics Box (fig. 31D). Remove the screw on the other side of the Electronics Box (fig. 31E). The Electronics Box is now ready to open up.

Figure 31 Removing the Electronics Box from the Ender 3 base. A) Overview of the underside of the base. B) Y limit switch connector. C) M5x45 screws, holding the base to the buildplate. D) One of the two mounting screws. E) Second mounting screw. F) The detached Electronics box.

### Step 30: Removing the Electronics Board and cable restrictions

All the redundant connectors from the Electronics Board have to be removed. To do this, open up the Electronics Box (fig. 31A). Remove the screws holding the board in place (fig. 31B). Note the yellow circle, indicating the fan connector. The fan is temporarily removed to facilitate this and the next step. Next, cut the zip tie on the cable assembly (fig. 31C). Finally, remove the tape at both ends of the braided cable shield (fig. 31D).

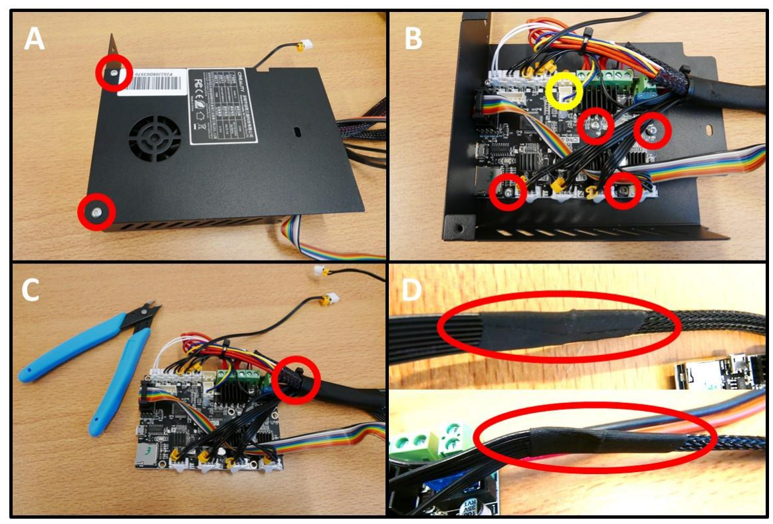
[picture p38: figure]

Figure 32 Freeing up the cable assembly to remove redundant cabling. A) Opening the Electronics Box. B) Removing the board mounting screws. Yellow circle indicates the removed fan connector. C) Cutting the zip tie. D) Removing the tape at the braid ends.

### Step 31: Removing redundant cables

All cables along the top row of the Electronics Board can be removed, as well as the blue/yellow cable. These are indicated in red (fig. 33A). The board after removal of these cables is shown in fig. 33B. Next, remove the short Z stepper cable and replace it with the long E stepper cable.

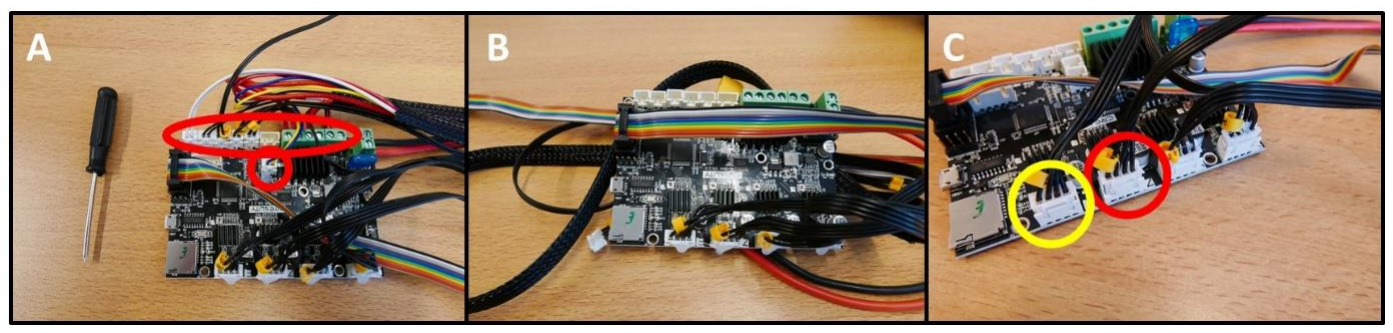
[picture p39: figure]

Figure 33 Removal of redundant cables. A) All cables to remove are indicated in red. B) After cable removal. C) Remove the Z stepper cable (red) and replace with the E stepper cable (yellow).

### Step 32: Collect the components for the Control Unit

To build the control unit, take the Power Supply Unit (PSU), LCD Screen, 40x40 rail, Electronics Box and Board, bag of four M5x8 screws, bag of two M4x20 screws, X Belt Tensioner, six M3x6 screws from the Electronics box, the PSU base 3D print and Electronics Base 3D print (fig. 34).

Figure 34 Overview of parts for the Control Unit.

### Step 33: Install the LCD on the 40x40 rail

Using 2 M5x8 screws, install the LCD on the 40x40 rail (fig. 35).

Figure 35 LCD mounted on the 40x40 rail.

### Step 34: Install the PSU on the 40x40 rail

To install the PSU Mount on the 40x40 rail, take the M4 screws and M4 T nuts from the X Belt Tensioner (fig. 36A). Slide the T nuts into the bottom track of the 40x40 rail and put the screws into the counterbored holes (fig. 36B). Tighten the screws to affix the PSU Mount. Next, put the M4x20 from the plastic bag into holes to mount the PSU (fig. 36C). The PSU is now fixed to the rail.

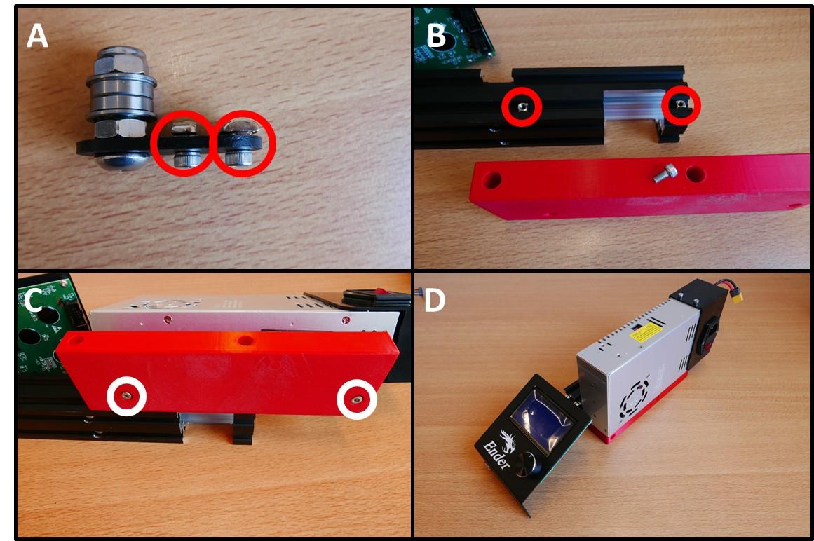
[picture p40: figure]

Figure 36 Installing the PSU on the 40x40 rail. A) Reuse the M4 screws and T nuts from the X Belt Tensioner. B) Insert T nuts into the rail and screws into the PSU mount. Tighten the screws. C) Screw the PSU to the PSU mount using the M4x20 screws. D) PSU mounted to the 40x40 rail.

### Step 35: Rebuild the Electronics Box

The Electronics Box needs to be rebuilt before mounting it on the Control Unit. Put the board back in the case using the previously removed M3x6 screws. Reattach the fan connector (fig. 37A). Put the cover back in place with the remaining M3x6 screws (fig. 37B).

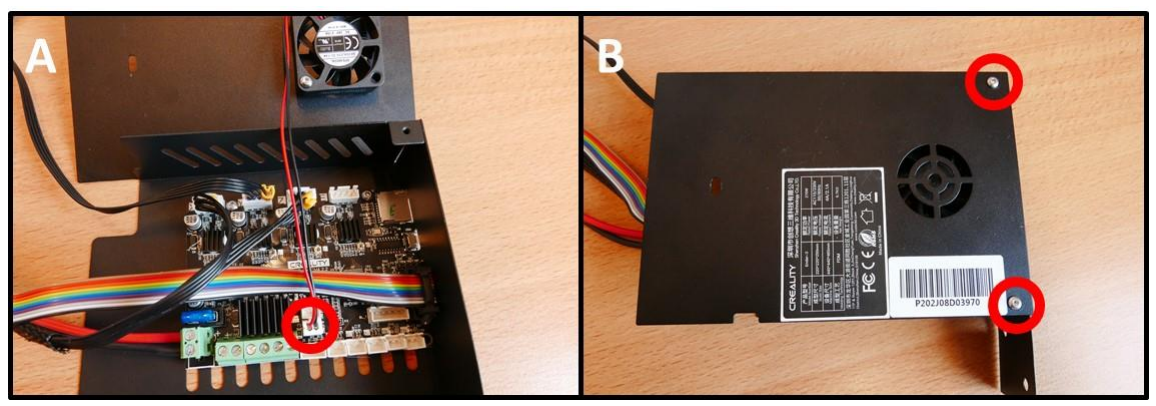
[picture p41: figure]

Figure 37 Rebuilding the Electronics Box. A) Electronics Board back in place, fan reattached. B) Cover replaced.

### Step 36: Attach the Electronics Base and Electronics Box

To attach the Electronics Box and Electronics Base, sandwich the mounting plates and attach them to the free end of the 40x40 rail (fig. 38A) using two M5x8 screws. Attach the Electronics Board to the PSU (fig. 38B). Attach the rainbow colored cable to the rightmost LCD connector (above the 40x40 rail) (fig. 38C).

Figure 38 Attaching the Electronics Box to the Control Unit. A) Attach the Electronics Box and Electronics Base. B) Connect to the PSU. C) Attach the rainbow colored cable to the LCD.

### Step 37: Attach the stepper motors to the Control Unit

The final step in the assembly process is to connect the stepper motor cables to the stepper motors themselves. The final result is shown in figure 39. The pump system is now completely built and ready to use.

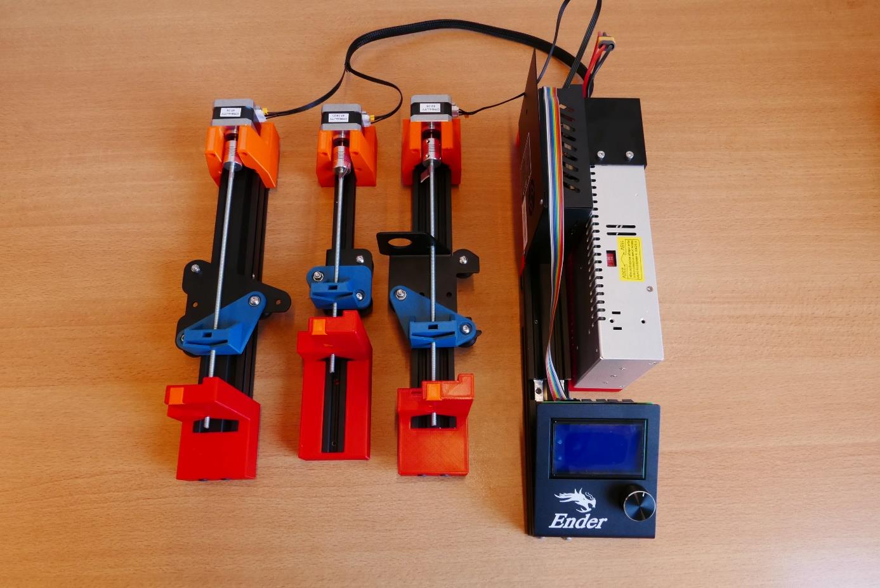
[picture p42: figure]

Figure 39 The fully assembled pump system, with the stepper motor cables attached.

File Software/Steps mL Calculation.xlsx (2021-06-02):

Part Description | Type | Step angle (deg) | Microstep | Pitch (mm)
Stepper Motor | BJ42D15-26V09 | 1.8
Stepper Driver | TMC2208 |  | 16
Leadscrew | M5x0.8 |  |  | 0.8
 |  |  |  | Steps/mm | 4000
 |  |  |  | Min. Movement (mm) | 0.00025
Fill in the inner diameter (ID) of syringe
Syringe | ID (mm) | Area (mm^2) | V/mm (mL) | V/step (mL) | Steps/mL (n)
1 mL | 4.7 | 17.34944543 | 0.01734944543 | 4.337361357e-06 | 230554.9198
5 mL | 12.3 | 118.8228881 | 0.1188228881 | 2.970572204e-05 | 33663.54801
10 mL | 15.6 | 191.134497 | 0.191134497 | 4.778362426e-05 | 20927.67168
20 mL | 20.1 | 317.308712 | 0.317308712 | 7.9327178e-05 | 12606.0201

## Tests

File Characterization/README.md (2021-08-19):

# Pressure fluctuation of the Ender 3 syringe pumps: 

Thanks to Rahat Haque and Maiwenn Kersaudy-Kerhoas (https://www.ed.ac.uk/infection-medicine/our-staff/associate-members/dr-maiwenn-kersaudy-kerhoas-profile) who have measured the pressure fluctuation of the Ender 3 syringe pumps using their developed methodology, which you can read it here: https://aip.scitation.org/doi/full/10.1063/5.0057415

The outcome is that the the open-source ENDER pump performs as well as the Aladdin pump (classical red syringe pumps) over a large range of flow rate and pressures, at a fraction of the price. It should be noted that it is not suitable for precise operation. 

The PDF summarise the results, which can be seen also on PubPeer: https://pubpeer.com/publications/B181F8CA9FC58E82DFA00AC1A47487

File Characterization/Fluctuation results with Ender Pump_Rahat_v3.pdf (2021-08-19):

# Characterisation of Ender pump pressure fluctuations against 3 commercial pumps

Rahat Haque, Maïwenn Kersaudy-Kerhoas

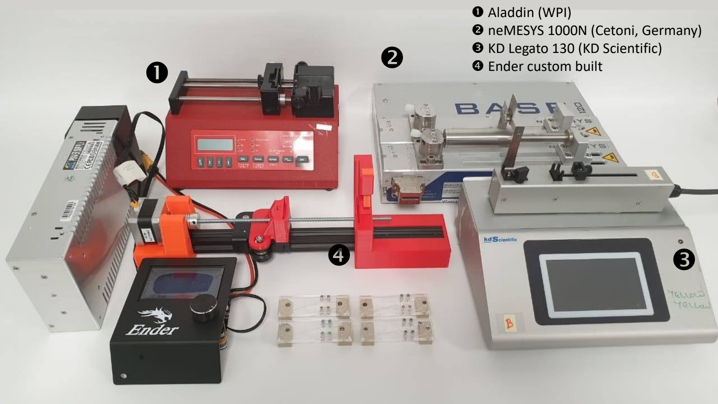
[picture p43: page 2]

Aladdin (WPI)
neMESYS 1000N (Cetoni, Germany) KD Legato 130 (KD Scientific)
Ender custom built

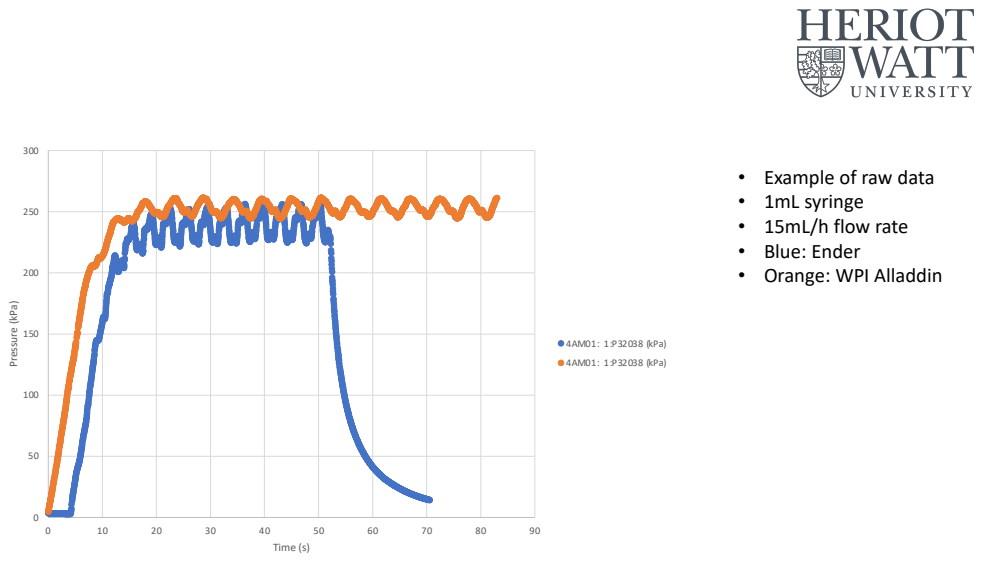
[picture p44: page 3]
Pressure (kPa); Time (s); 4AM01: 1:P32038 (kPa)

• Example of raw data • 1mL syringe • 15mL/h flow rate • Blue: Ender • Orange: WPI Alladdin

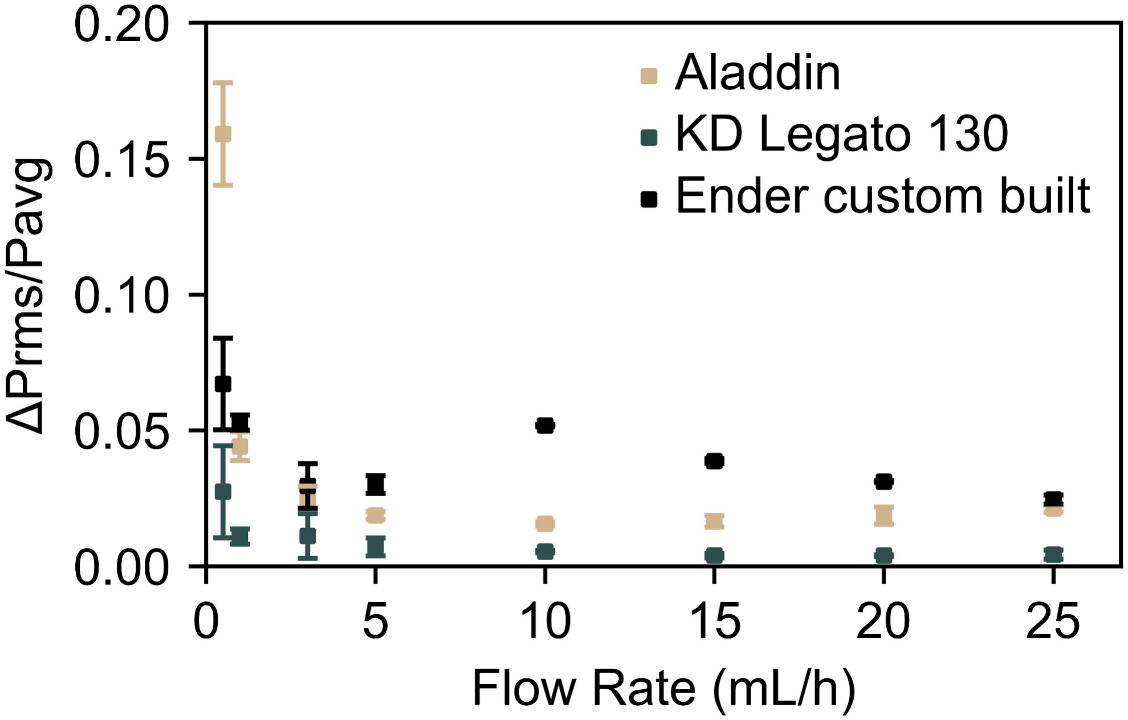
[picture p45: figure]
• 1 mL syringe experiment for a single device using 3 different pumps • Price: Ender<Aladdin<<<KD Legato; KD legato

- Relative fluctuation: Ender> Aladdin>>
- Micro steps per revolution: • Ender: 200 • Aladdin: 400 • KD: 3200
- Characterisation of pressure fluctuations of KD Legato, Aladdin and Ender custom built pumps using Feb16 B1 blood plasma separation device
- 1mL syringes • N=3 for all points • Note: only Ender ‘X pump’ was used

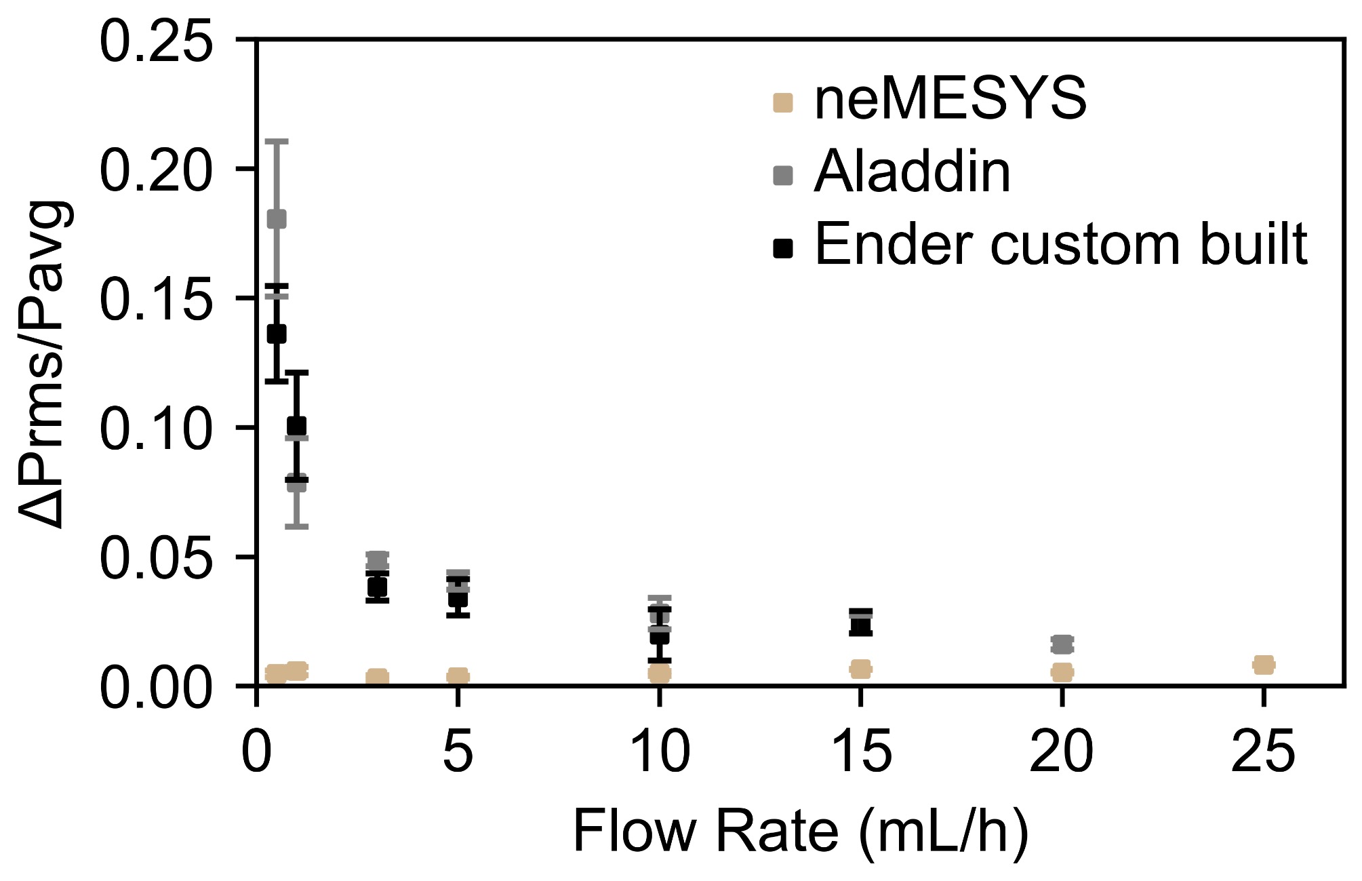
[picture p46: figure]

- Characterisation of pressure fluctuations of neMESYS, Aladdin and Ender custom built pumps using Feb16 B1 blood plasma separation device
- 5mL syringe
- N=3 for all points
- Note 1: neMESYS does not accept 1mL syringes, while KD Legato does not accept 5mL syringes
- Note 2: Only Ender ‘Y pump’ was used
- Note 3: Back pressure was too high for the Ender pump to pump at 20 or 25 mL/h (~400 KPa)

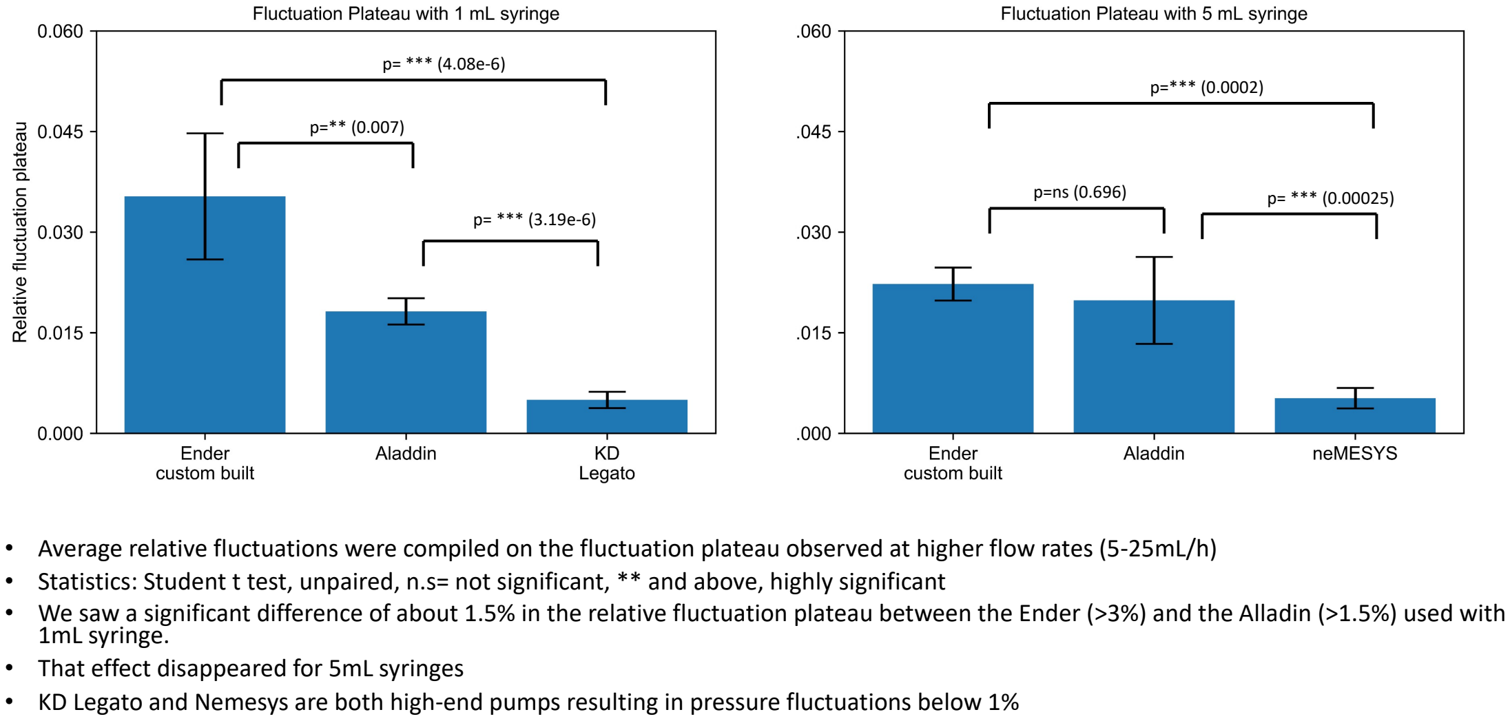
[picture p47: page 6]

p=** (0.007)

p= *** (3.19e-6)

p=ns (0.696) | p= *** (0.00025)

p= *** (4.08e-6)
p=*** (0.0002)
- Average relative fluctuations were compiled on the fluctuation plateau observed at higher flow rates (5-25mL/h)
- Statistics: Student t test, unpaired, n.s= not significant, ** and above, highly significant
- We saw a significant difference of about 1.5% in the relative fluctuation plateau between the Ender (>3%) and the Alladin (>1.5%) used with 1mL syringe.
- That effect disappeared for 5mL syringes
- KD Legato and Nemesys are both high-end pumps resulting in pressure fluctuations below 1%

- Pulseless neMESYS syringe pump (>£12K) has the lowest frequency and for the full range, the relative fluctuation is limited within 0.2 to 0.6%, unlike the stepper motor-based syringe pumps.
- The KD pump (~£3k) shows the lowest relative fluctuation among the stepper motor-based syringe pumps. Although it provides 0.5% relative fluctuation after reaching the plateau after 5 mL/h flow rate (corresponding frequency 0.12 Hz), at lower flow rates it can provide higher fluctuation( e.g., 3% fluctuation at 0.5 mL/hour).
- The widely used Aladdin syringe pump (~£500), which retails at 16% of the cost of the KD pump provides much more fluctuations than the KD syringe pump at plateau [~4.5 times].
- Overall, the open-source ENDER pump (£140) performs as well as* the Aladdin pump, at a fraction of the price, but is not suitable for precise operation. It is preferable to use to 5mL syringes or above, and avoid flow rates below 1mL/h
- Additional note: we noticed significant deviations on the Ender pump at lower flow rates, typically lower than 1mL/h. We cannot be more precise than this at this stage, we would need to invest more time to look into this. Would you be interested in this at all?

# Conclusions

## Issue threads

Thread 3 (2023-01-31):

### ISSUE TITLE
Various Syringe sizes simultaneously

### ISSUE THREAD

**Issue by YTayyar** [Vsaggiomo/Ender3-syringe-pumps#3]
Hi and Thank you for the amazing work.
Is it possible to use different syringe pumps on the different channels at once?
Also, can you specify a certain flow rate for each channel at the same time?

**Comment by Vsaggiomo** [comment]
Yes, it is possible to use different syringes on different pumps, you just need to change the M92 commands, and yes it is possible to use different flow rates for each channel. From our paper: 
________
Multiple syringes can be used at the same time:

G1 X0.5 Y0.5 Z0.5 F1

Will deliver, at the same time, 0.5 mL of liquid from the pumps on X, Y, and Z at a speed of 1 mL/min

For using different flow speed for different pumps, the total amount of liquid should be calculated taking in account that all the pumps will reach the end at the same time. For example:

G1 X2 Y1 Z2 F1

Will deliver the set amount of liquid at different flow speed, using 1 mL/min on Y, and 2 mL/min on X and Z.
__________

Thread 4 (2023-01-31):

### ISSUE TITLE
False or no response 

### ISSUE THREAD

**Issue by MjacobG** [Vsaggiomo/Ender3-syringe-pumps#4]
Hello! Thank you very much for your tutorial, this is an awesome project! I am trying to replicate the project using one stepper motor.  The motherboard I am using is the Creality3D  V1.1.4 which belongs to my old Ender 3 Pro. The firmware of the V1.1.4 has been upgraded to the "TH3D U1.R2.A8". The stepper motor I use is a Creality 40-42 with official stepper drivers . The lead screw is 8mm in diameter and has 2mm thread Pitch (looks like the original z axis).

I tried to run your gcode, slightly modified like this: 

Line1: ; Experiment 01 27/01/2023
Line2: ; 5 mL syringe, one pump
Line3: ; ID of 5 mL syringe is 12.4 mm
Line4:
Line5: M92 Z-33123 ; set the proper steps/mL for the 5mL syringe!
Line6:
Line7: M302 S0 ; print without checking temperature 
Line8: M211 S1 ; print with checking the Z end stop 
Line9: G91 ; relative positioning 
Line10: ; deliver 1mL at 1mL/min sequentially 
Line11: G1 Z1 F1 
Line12: ; wait for 10 seconds
Line13: G4 S10
Line14: ; reverse movement
Line15: G1 Z-1 F1 

Result: 
1. The pusher block starts immediately and moves backwards until it hits the Z end stop. Then, after 10 seconds, the pusher block moves forward (towards the syringe, that's good) for 1 minute covering a distance of 8.7 cm. Exceeds the length of a 5ml syringe. 
2. When Line11 is inactive ( ;G1 Z1 F1 ), nothing happens
3. When Line15 is inactive ( ;G1 Z-1 F1 ), the gcode stopes after the push block hits the z end stop.
4.  The 33123 value, obtained from your excel file after replacing the ID of my 5ml syringe. 

I am confused because I would like to simple have a flow of 1ml in 1ml/min and the results are not even close to the ideal scenario.

I would appreciate any valuable feedback! 
Thank you in advance, 
Jacob

**Comment by Vsaggiomo** [comment]
Hi there, I see multiple problems there :) 

1) First of all you are using another firmware and I'm not sure if it's going to work. It should, but you never know. 

2) You are using a screw that is different from what we use. As the linear motion is dictated by the pitch of the screw, the M92 command is clearly wrong. You can calculate it here https://blog.prusa3d.com/calculator_3416/ if it's a standard screw. Or you can just put a number in the M92 and try to move the axis of 5cm and adjust that number until you reach exactly a motion of 5mc. 

3) Most probably you are running a faulty gcode on the sd card. There should be no empty line and it should be written with a proper text editor, for example notepad++ using EOL (end of line) from Unix. I would start from proterface, using a USB cable and check with the computer.

**Comment by MjacobG** [comment]
Thank you very much for your prompt response! In fact the solution was very easy and right in front of my eyes! After your 2nd commend I just realized that I use an identical copy of the original z-axis lead screw. So, I deleted the M92 code and using the cylinder volume function, I solved for l (length) and I found that in order to dispense 1ml, the push block has to move 8.15mm. So the G-code Was just one line code: 
G1 Z8.15 F1 
Know I have to calculate the right F speed. Thank you very for your comments :)

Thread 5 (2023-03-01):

### ISSUE TITLE
Functionality Based on Direction

### ISSUE THREAD

**Issue by NikiW94** [Vsaggiomo/Ender3-syringe-pumps#5]
I am having issues getting the pump to function properly. I am 99% certain that it is exclusively a g-code problem, not something wrong with the actual assembly. First of all, for my first test of the system, I used the example g-code in the operating instructions* and only one of the three pumps (E) functioned. The other two did not rotate at all. The E pump, however, followed the code just fine. In my second test, I changed this line: M92 X-20927 Y-20927 Z20927 to this: M92 X20927 Y20927 Z20927 and kept the rest the same. All three pumps moved, but, as noted in the article, X & Y moved backward. In another test, I used the following code:
; 5 mL syringes on the three pumps
M92 X33663 Y33663 Z33663 ; set the proper steps/mL for the 5mL syringe
M302 S0 ; print without checking temperature
G91 ; relative positioning
; deliver 1mL at 2mL/min sequentially
G1 X1 F2
G1 Y1 F2
G1 Z1 F2
This time X & Y still moved backward but pump E did not move. Then, again, when I modified the first line to be M92 X-33663 Y-33663 Z33663, none of the pumps worked. I don't see another way to change the direction of the X & Y pumps without making them stop. Any suggestions would be highly appreciated.

____________________________________________________________________________________
*M92 X-20927 Y-20927 Z20927 ; set the proper steps/mL for the 10mL syringe
M302 S0 ; print without checking temperature
G91 ; relative positioning
; deliver 1mL at 2mL/min sequentially
G1 X1 F2
G1 Y1 F2
G1 Z1 F2
; wait for 10 seconds
G4 S10
; deliver 1mL on X and Z at 1mL/min, 2mL on Y at 2mL/min
G1 X1 Y2 Z1 F1
; wait 10 seconds
G4 S10
; deliver 1mL at 2mL/min sequentially
G1 Z1 F2
G1 Y1 F2
G1 X1 F2

**Comment by Vsaggiomo** [comment]
well, juts to be pragmatic and make the system work, you can keep the M92 positive and then move the X Y motors in negative :) 
M92 X33663 Y33663 Z33663
M302 S0 ; print without checking temperature
G91 ; relative positioning
G1 X-1 F2
G1 Y-1 F2
G1 Z1 F2

then you talk about the E motor, but in none of the example you wrote, you use it (G1 E), so, not sure about that. 

to solve the problem once for all, my guess is that is a text editor problem (try to use notepad++) as gcode files may be annoyed by some hidden characters (for example there is - and – which are two different characters)
I'd say, try to connect the motherboard with prontface and give the commands one by one and check where is the problem.

**Comment by NikiW94** [comment]
Hello. Thanks for your response. Just to clarify, in my first comment when I referred to pump "E" in the g-code it is designated as pump "Z" but the cable is labeled as "E". I will refer to it as pump Z moving forward. 

I have a new set of questions based on experimentation/troubleshooting that I have done today. 

First of all, sometimes when something goes wrong the LCD displays "Heating failed PRINTER HALTED Please reset". The only way I have found to "reset" the system is to turn it off and back on. Is there another method? Or is that practice okay? Has this ever occurred when you were initially testing the pump?

Second, I connected the system to Pronterface as you suggested and I think I understand the problem, but I have no idea how to resolve it. I began by inputting M92 X33663 Y33663 Z 33663. Then M302 S0 and G91. After those were all sent, I input G1 X1 F2. That worked just fine; the motor was just inverted as before. Then I tried G1 X-1 F2 and received this error message: 

echo: endstops
hit: X:1.00

I understood this to mean the system doesn't know where it is in space, so I clicked the home button just to see what would happen and all three motors emitted this grinding sound and didn't rotate smoothly so I killed that command. 

In another test I input M92 X-33663 Y-33663 Z33663, M302 S0, G91, which all sent without throwing any errors. After G1 X1 F2, I then received the following message:

echo: endstops
hit: X:0.00

In the last test I input M92 X33663 Y33663 Z33663, M302 S0, G91, and G1 X1 Y2 Z1 F1. That worked (inverted again), but when I changed the last instruction to G1 X-1 Y-2 Z1 F1, I got:

echo: endstops 
hit:  X:3.00 Y:4.00

Also, I don't know if this is relevant, but each time Pronterface threw and error, I could hear the motors switch on but none of the pumps moved. 

I wondered if you had any insight as to how I can fix this. Thanks.

**Comment by Vsaggiomo** [comment]
I see, you missed: 
M211 S0 ; print without checking the end stops 
it should go after the M302 S0 
:) 

please tell me if this fixed it so I can close this issue

**Comment by NikiW94** [comment]
So, I added M211 S0 to the line up so my test code now looks like this:

M92 X33663 Y33663 Z33663
M302 S0
M211 S0
G91
G1 X-1 F2

And I am still thrown this error message:

echo: endstops hit:  X:1.00

In case it is relevant, when I a sent M211 S0 into Pronterface, it returned:

echo: Soft endstops: Off  

Did I do something wrong? For further context, if I input G1 X1 F2 it still runs, just backwards as before.

I appreciate your help.

**Comment by Vsaggiomo** [comment]
ok, that's weird, what happens if you give the commands line by line in pronterface?
are you sure the physical endstops are not installed? 
or you can try M121 before the M211 S0 

also, in pronterface can you send an M115 and tell me which firmware is installed there?

**Comment by NikiW94** [comment]
The system that I physically built was done so using the provided instructions. I took no creative liberties. When you say physical endstops do you mean the motor mount and syringe mount 3d printed pieces?

>>> M92 X33663 Y33663 Z33663
SENDING:M92 X33663 Y33663 Z33663
>>> M302 S0
SENDING:M302 S0
>>> M211 S0
SENDING:M211 S0
echo:Soft endstops: Off  Min: X0.00 Y0.00 Z0.00  Max: X235.00 Y235.00 Z250.00
>>> G91
SENDING:G91
>>> G1 X-1 F2
SENDING:G1 X-1 F2
echo:endstops hit:  X:7.00

Above is everything I just put into Pronterface and the returned messages. 

Below is everything I get when I input M115:

>>> M115
SENDING:M115
FIRMWARE_NAME:Marlin Creality 3D SOURCE_CODE_URL:https://github.com/MarlinFirmware/Marlin PROTOCOL_VERSION:1.0 MACHINE_TYPE:Ender-3 EXTRUDER_COUNT:1 UUID:cede2a2f-41a2-4748-9b12-c55c62f367ff
Cap:EEPROM:1
Cap:AUTOREPORT_TEMP:1
Cap:PROGRESS:0
Cap:PRINT_JOB:1
Cap:AUTOLEVEL:0
Cap:Z_PROBE:0
Cap:LEVELING_DATA:0
Cap:SOFTWARE_POWER:0
Cap:TOGGLE_LIGHTS:0
Cap:CASE_LIGHT_BRIGHTNESS:0
Cap:EMERGENCY_PARSER:0

I also tried: 
; 10 mL syringes on the three pumps
M92 X-20927 Y-20927 Z20927 ; set the proper steps/mL for the 10mL syringe
M302 S0 ; print without checking temperature
M121
M211 S0 ; print without endstops
G91 ; relative positioning
; deliver 1mL at 2mL/min sequentially
G1 X1 F2
G1 Y1 F2
G1 Z1 F2

This, I am happy to report, worked just fine. The only problem with the above is that I have to load it into Pronterface for it to function. If I save it on a microSD and print it using the LCD, the Z pump doesn't move. Don't know what that's about. But I suppose I can just use it tethered to a computer.

**Comment by Vsaggiomo** [comment]
Perfect, then I'll close it here. For the SD card, I'm 99% sure it's a text formatting thing. You should have no spaces or weird characters (they may be invisible, but happens because of copy/paste). And you need to use a proper text editor, like notepad ++ . In notepad ++ you need to use "UNIX" end of the line:
 End of Line (EOL) characters used on Windows vs Unix. Using Edit > EOL Conversion > Unix (LF), to switch to the Unix EOF character.

**Comment by Vsaggiomo** [comment]
Summary: 
weirdly enough, this combo firmware/board had a problem with the endstops, and they were triggered even if the M211 S0 (print without soft end stop) was in there. 
The command M121 (Disable endstops) did the trick and the pumps work correctly now

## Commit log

2021-06-02 build guide v0.1
    [Clamp Bar Long v1.f3d, Clamp Bar Long v1.stl, Clamp Bar Short v1.f3d, Clamp Bar Short v1.stl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]
2021-06-15 Added STEP files
    [Clamp Bar Long v1.step, Clamp Bar Short v1.step, Clamp Bar v1.step, Dovetail Cap v1.step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]
2021-07-10 Ender 3 V2 PSU adaptor
    [psu_mount_Ender3v2.scad, psu_mount_Ender3v2.stl]
2021-11-05 Added 50mL syringe adaptors
    [E End Mount 50 mL v2.stl, X X Motor End Mount 50mL v2.stl]
2021-11-11 added double syringe files
    [E End Mount 50 mL.f3d, E End Mount 50 mL.stl, E End Mount Dual 50 mL.f3d, E End Mount Dual 50 mL.stl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]
2022-07-06 Added designs for bigger shaft couplers
    [E Stepper Mount Large Shaft Coupler v1.stl.stl, X X Motor Stepper Mount Large Shaft Coupler v1.stl]
2024-04-11 Updated dual+50mL
    updated files for the dual syringe and the dual 50mL
    [E End Mount Dual 50 mL v1.f3d, E End Mount Dual 50 mL v1.step, E End Mount Dual 50 mL v1.stl, E End Mount Dual 50 mL.stl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]
